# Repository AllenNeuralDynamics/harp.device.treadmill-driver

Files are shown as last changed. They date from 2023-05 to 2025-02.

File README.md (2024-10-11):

A Harp Device for controlling an instrumented variable-friction mouse treadmill

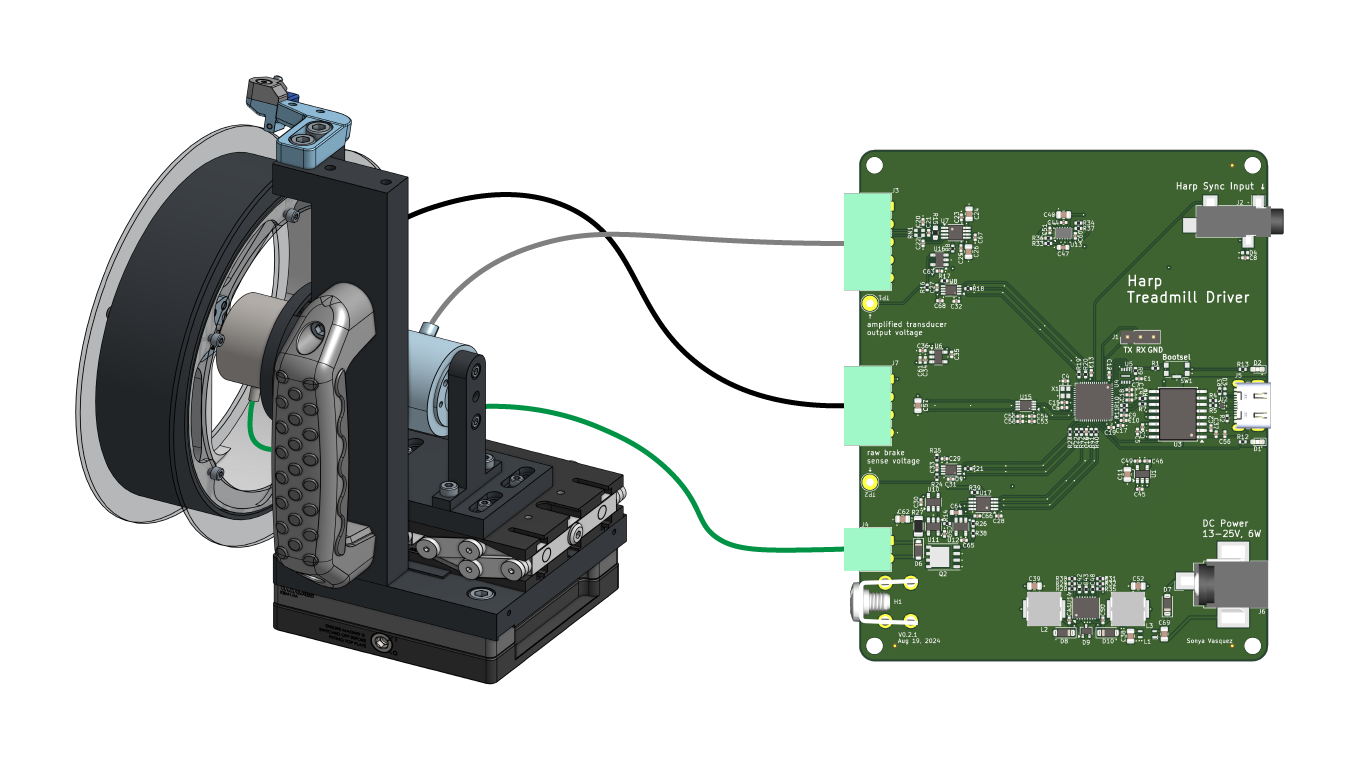
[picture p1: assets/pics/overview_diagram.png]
overview


> [!NOTE]
> This repository contains design files for the electronics assembly. For the mechanical assembly, design files, and bill-of-materials, see the [OnShape project](https://cad.onshape.com/documents/579ff6de692121d8b6a45604/v/23e1e086e9eb645d096dac80/e/a0ad881c32324c0acf8e15df).

## Features
* linear (no switching!) current control of 12V magnetic brake, Placid Industries B5ZD, [datasheet](https://placidindustries.com/d/?h=a03be4b).
* reads measurements from an [RTS-10 torque transducer](https://www.transducertechniques.com/rts-torque-sensor.aspx#)
* wheatstone bridge input for torque transducer
* quadrature encoder input for position/speed measurements
* Harp-protocol compliant over full-speed USB
* accepts Harp time synchronization input.
* reverse-polarity protected power supply.

## Register Map
[List of Registers](./firmware/docs/register_map.csv)

## Credits
This board design was created in partnership with the team at [Second Order Effects](https://soeffects.com/).

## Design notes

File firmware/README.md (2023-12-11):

## Setting up the Build Environment

### Install Submodules
This project uses the [Harp Core RP2040](https://github.com/AllenNeuralDynamics/harp.core.rp2040) library as a submodule.
Install it with:
````
git submodule update --init
````

### Install Pico SDK
This project uses the [Pico SDK](https://github.com/raspberrypi/pico-sdk/tree/master).
The SDK needs to be downloaded and installed to a known folder on your PC.
Note that the PICO SDK also contains submodules (including TinyUSB), so you must ensure that they are also fetched with:
````
git clone git clone git@github.com:raspberrypi/pico-sdk.git
git submodule update --init --recursive
````

### Point to Pico SDK
Recommended, but optional: define the `PICO_SDK_PATH` environment variable to point to the location where the pico-sdk was downloaded. i.e:
````
PICO_SDK_PATH=/home/username/projects/pico-sdk
````
On Linux, it may be preferrable to put this in your `.bashrc` file.

## Compiling the Firmware

### Without an IDE
From this directory, create a directory called build, enter it, and invoke cmake with:
````
mkdir build
cd build
cmake ..
````
If you did not define the `PICO_SDK_PATH` as an environment variable, you must pass it in here like so:
````
mkdir build
cd build
cmake -DPICO_SDK_PATH=/path/to/pico-sdk ..
````
After this point, you can invoke the auto-generated Makefile with `make`

## Flashing the Firmware
Press-and-hold the Pico's BOOTSEL button and power it up (i.e: plug it into usb).
At this point you do one of the following:
* drag-and-drop the created **\*.uf2** file into the mass storage device that appears on your pc.
* flash with [picotool](https://github.com/raspberrypi/picotool)

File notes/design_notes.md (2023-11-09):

## RP2040

### Oscillator
The RP2040 accepts either a crystal or CMOS-level clock input
I opted for a precision oscillator instead of a vanilla crystal.
To preserve USB Boot functionality (useful!), I kept the frequency at 12MHz (datasheet pg 12).

This oscillator requires a 0.01-0.1uF bypass capacitor placed very close to the pins.
An example layout is provided in the datasheet.

## USB Isolator
To disconnect the host PC's ground from this device's ground, I added a Full-Speed capable USB isolator.

The downside is that this device cannot be powered via USB from the host pc.

## Analog Front-End

# PCB Layout

## Layers

## References
* [All About USBC: Example Circuits](https://hackaday.com/2023/08/07/all-about-usb-c-example-circuits/)
  * contains schematic for a device to display itself as a full speed USB device.
* [Raspberry Pi Pico Datasheet](https://datasheets.raspberrypi.com/pico/pico-datasheet.pdf)
  * contains schematic for minimal board design.
* [AD9833 Signal Generator First Steps Part 1](https://daumemo.com/diy-ad9833-signal-generator-first-steps-part-1/)
  * Contains effect of load resistance on output voltage.
* [Hardware Design with the RP2040](https://datasheets.raspberrypi.com/rp2040/hardware-design-with-rp2040.pdf)
* [SPI: High Speed Design](https://practicalee.com/spi/)
  * source termination resistor placement.
* [Reduced Printed Circuit Board Emissions with Low-Noise Design Practices](https://ntrs.nasa.gov/api/citations/20120009353/downloads/20120009353.pdf)
* [Stack Exchange: How to Connect USB Connector Shield](https://electronics.stackexchange.com/questions/4515/how-to-connect-usb-connector-shield)
* [Driving Inductive Loads with Power Switches](https://www.ti.com/video/6018730150001#transcript-tab)
* [B5ZD Magnetic Particle Brake datasheet](https://placidindustries.com/d/?h=a03be4b)
  * this design is intended for the 12V variant.
* [Signal Chain Basics 78: How to avoid common mode limitations on instrumentation amplifiers](https://www.planetanalog.com/signal-chain-basics-78-how-to-avoid-common-mode-limitations-on-instrumentation-amplifiers/)
* [Hammond Manufacturing 1455L801 Case Drawing](https://www.hammfg.com/files/parts/pdf/1455L801.pdf)

### Reference Designs
* [LTC2641 Datasheet](https://www.analog.com/media/en/technical-documentation/data-sheets/26412fd.pdf)
  * features a programmable constant current sink in the "Typical Application" section.

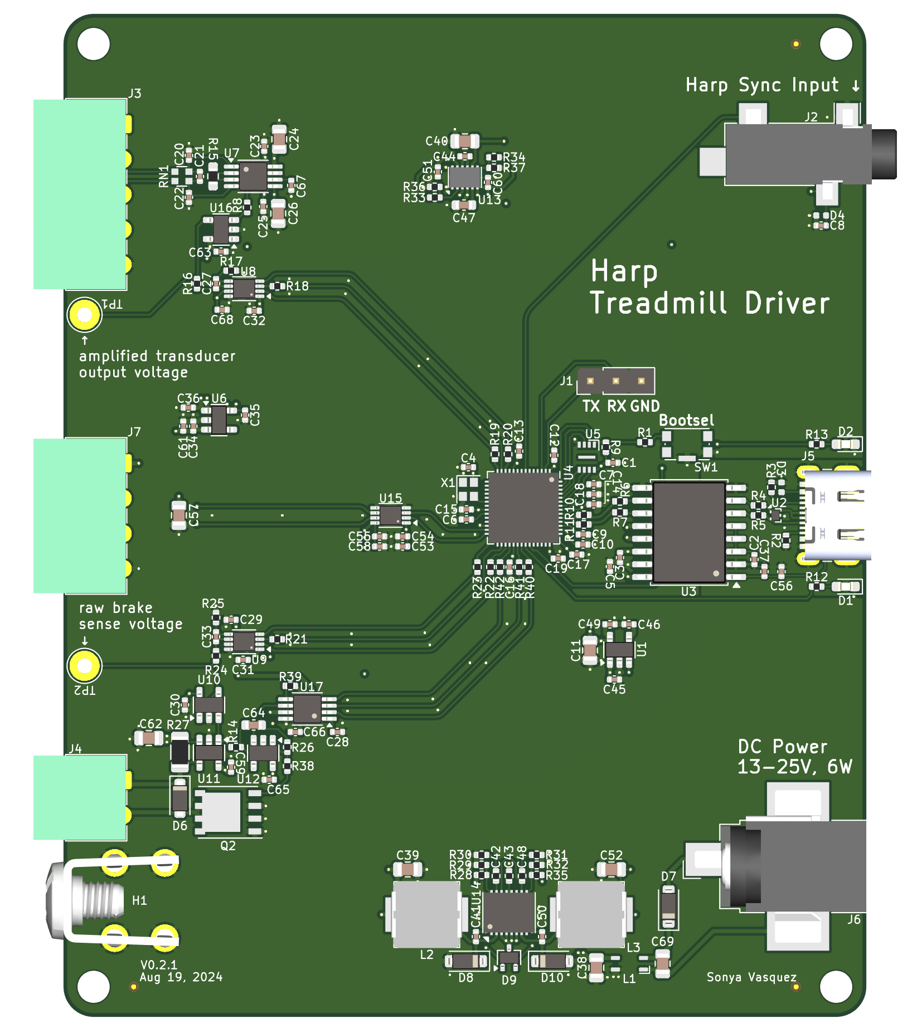
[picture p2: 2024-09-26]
assets/pics/treadmill_no_background.png

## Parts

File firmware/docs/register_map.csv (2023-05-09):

Register | Size | Read-Only | Name | Description
0x32 | U16 |  | TORQUE_SENSOR_RAW | raw measurement of the treadmill angular torque sensor.
0x33 | U16 |  | TORQUE_LOAD_CURRENT_RAW | raw measurement of the output current applied to the variable torque load.
0x34 | U32 |  | ENCODER_MEAS_RAW | raw measurement of the treadmill encoder (800 ticks per revolution).
0x35 | U32 |  | TORQUE_LOAD_SETPOINT_RAW | raw setpoint for the torque load.
0x36 | U8 |  | SUBSYSTEM_RESET | "Writing 1 to specific bits in this register will reset [0] the encoder count | [1] the torque load PI loop."

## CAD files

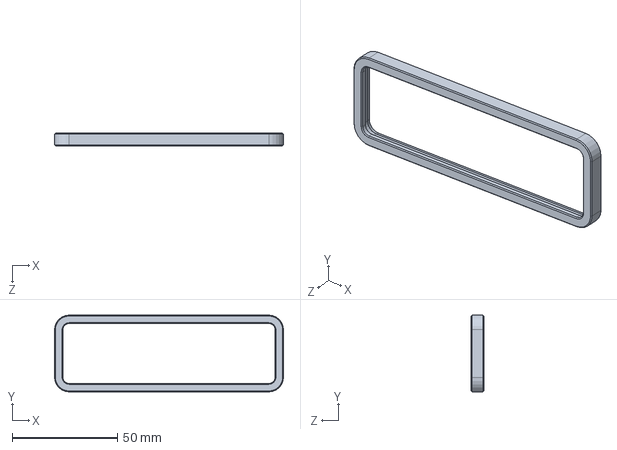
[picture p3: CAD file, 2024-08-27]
hardware/enclosure/cads/solidworks/1455L801_lids_and_trim.SLDPRT
108.9 x 36.5 x 6.00 mm

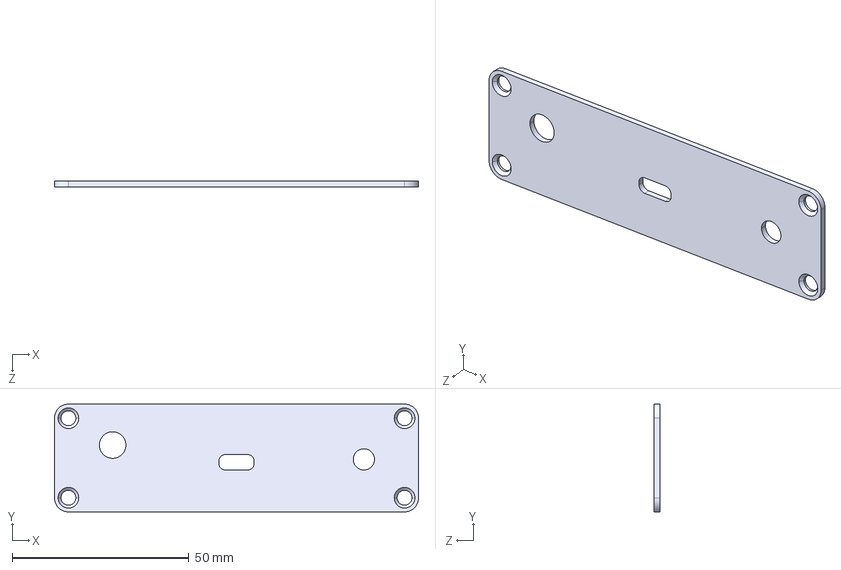
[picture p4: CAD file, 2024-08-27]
hardware/enclosure/cads/step/1455L801_lid_data_side.STEP
102.9 x 30.5 x 1.57 mm

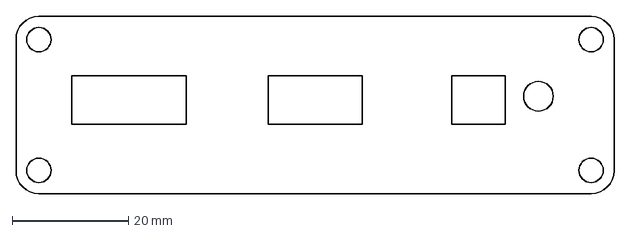
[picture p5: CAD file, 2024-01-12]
hardware/enclosure/exports/dxfs/1455L801_lid_io_side.DXF
102.9 x 30.5 mm

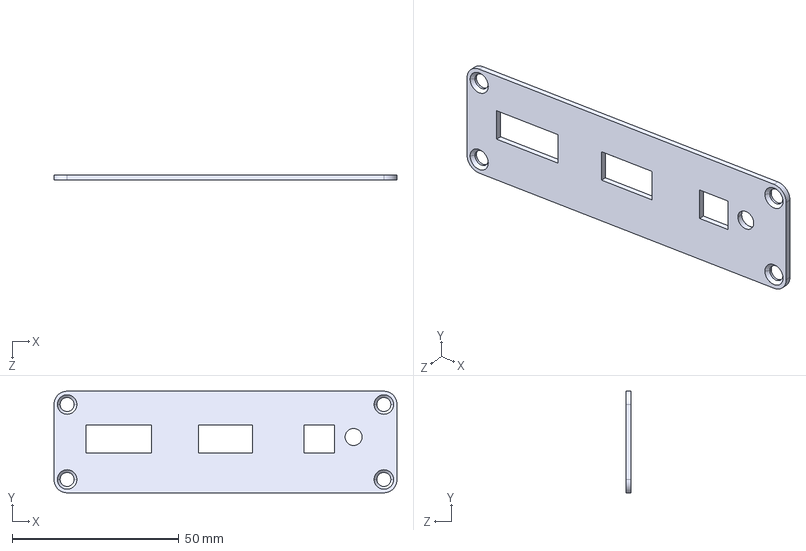
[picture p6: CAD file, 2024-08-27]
hardware/enclosure/cads/step/1455L801_lid_io_side.STEP
102.9 x 30.5 x 1.57 mm

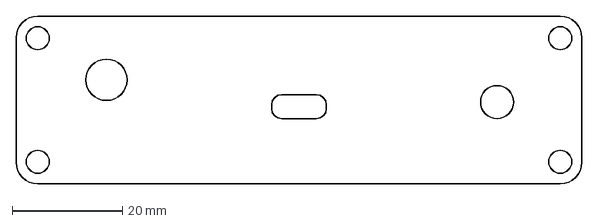
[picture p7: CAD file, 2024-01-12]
hardware/enclosure/exports/dxfs/1455L801_lid_data_side.DXF
102.9 x 30.5 mm

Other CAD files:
hardware/enclosure/exports/stls/1455L801_trim.STL

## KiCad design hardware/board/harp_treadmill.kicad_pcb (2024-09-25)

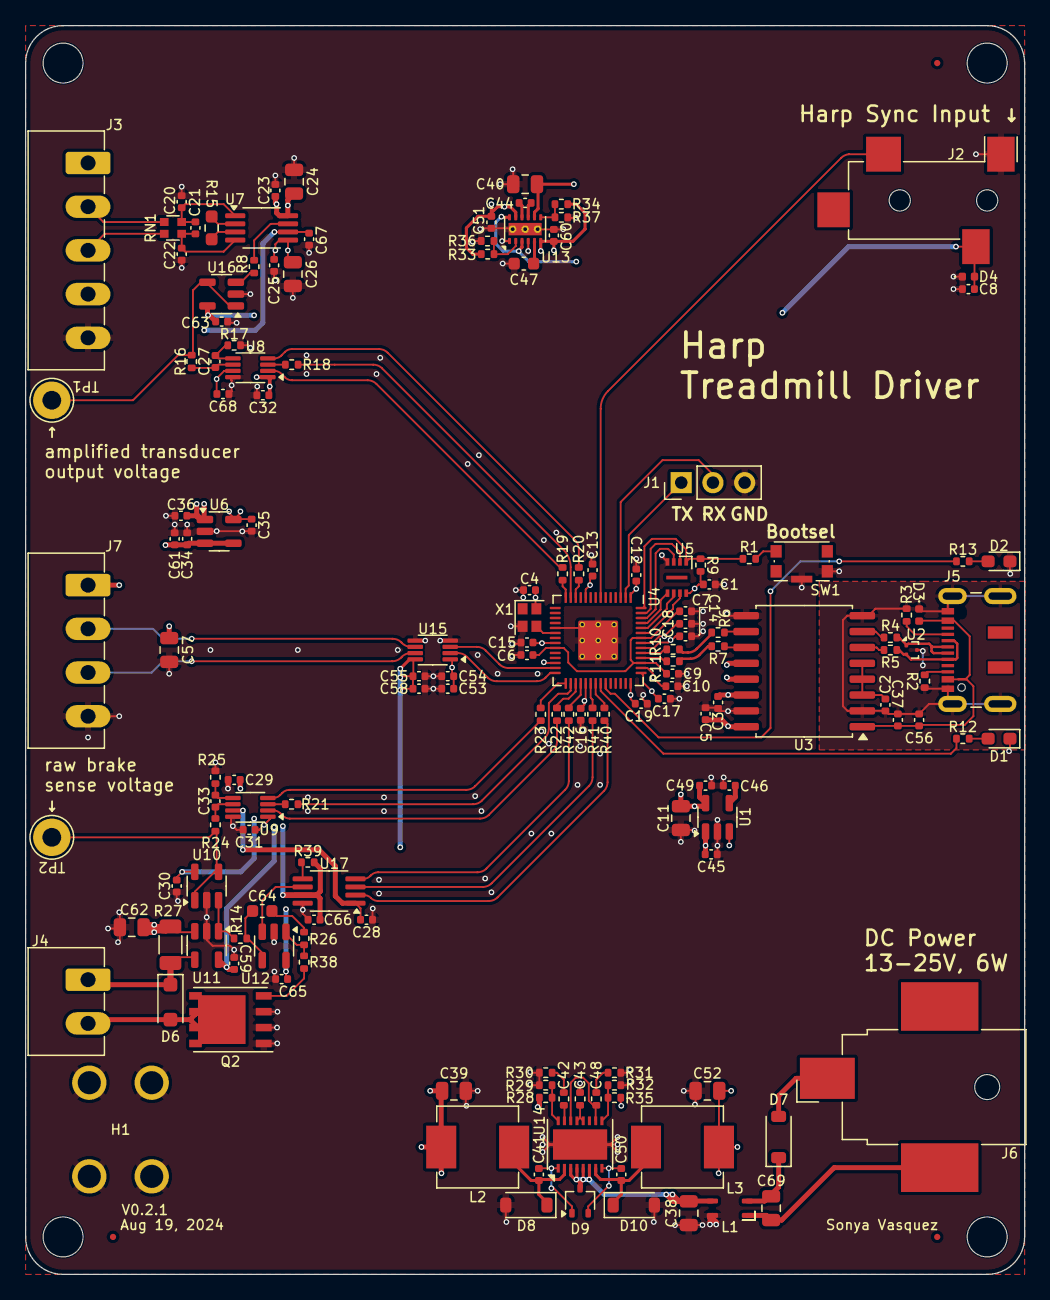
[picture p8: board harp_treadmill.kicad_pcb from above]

Board: 4 copper layers, 80.0 x 100.0 mm, 157 parts (0 on the bottom side), 105 nets.

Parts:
C1, C2, C3, C5, C6, C7, C12, C13, C14, C15, C16, C17, C18, C19, C23, C25, C28, C29, C30, C31, C32, C34, C35, C36, C37, C41, C50, C53, C58, C59, C63, C65, C66, C67, C68: 100nF; C_0402_1005Metric
C4, C46: 10nF; C_0402_1005Metric
C8, C9, C10, C44, C45, C54, C55, C56, C61: 1uF; C_0402_1005Metric
C11, C24, C26, C38, C57, C62, C69: 10uF; C_0805_2012Metric
C20, C22: 100pF; C_0402_1005Metric
C21: 1000pF; C_0402_1005Metric
C27, C33: 300pF; C_0402_1005Metric
C39, C40, C52: 22uF; C_0805_2012Metric
C42, C48: 1.5nF; R_0402_1005Metric
C43: 4.7nF; R_0402_1005Metric
C47: 4.7uF; C_0603_1608Metric
C49, C51, C60: 2.2uF; C_0402_1005Metric
C64: 10nF; C_0603_1608Metric
D1, D2: LED; LED_0603_1608Metric_Pad1.05x0.95mm_HandSolder
D3, D4: D_TVS; D_0402_1005Metric
D6: 1N4007FL; D_SOD-123F
D7, D8, D10: D_Schottky; D_SOD-123
D9: BAT54AW; SOT-323_SC-70
FID1, FID2, FID3: Fiducial; Fiducial_0.5mm_Mask1mm
H1: MountingHole_Pad; Terminal_Keystone_779x_EdgeMount_Horizontal
J1: Conn_01x03_Male; PinHeader_1x03_P2.54mm_Vertical
J2: AudioJack3; Jack_3.5mm_CUI_SJ-3524-SMT_Horizontal
J3: Conn_01x05_Female; PhoenixContact_MC_1,5_5-G-3.5_1x05_P3.50mm_Horizontal
J4: Conn_01x02_Female; PhoenixContact_MC_1,5_2-G-3.5_1x02_P3.50mm_Horizontal
J5: USB_C_Receptacle_USB2.0; USB_C_Receptacle_JAE_DX07S016JA1R1500
J6: Barrel_Jack_Switch; BarrelJack_CUI_PJ-036AH-SMT_Horizontal
J7: Conn_01x04_Female; PhoenixContact_MC_1,5_4-G-3.5_1x04_P3.50mm_Horizontal
L1: L_Coupled_1423; L_CommonModeChoke_TDKCorporation_1210
L2, L3: 10uH; L_Vishay_IHLP-2525
Q2: Si7336ADP; PowerPAK_SO-8_Single
R1: 1K; R_0402_1005Metric
R2, R3, R26: 5K1; R_0402_1005Metric
R4, R5, R6, R7: 24; R_0402_1005Metric
R8, R9, R28, R30, R31, R35, R39: 10K; R_0402_1005Metric
R10, R11: 27; R_0402_1005Metric
R12, R13: 680; R_0402_1005Metric
R14: 7K5; R_0402_1005Metric
R15: 499; R_0603_1608Metric_Pad0.98x0.95mm_HandSolder
R16, R17, R24, R25: 100; R_0402_1005Metric
R18, R19, R20, R21, R22, R23, R40, R41, R42: 49.9; R_0402_1005Metric
R27: 0.08; R_1206_3216Metric
R29: 715; R_0402_1005Metric
R32: 1K82; R_0402_1005Metric
R33: 162K; R_0402_1005Metric
R34: 158K; R_0402_1005Metric
R36, R37: 51K; R_0402_1005Metric
R38: 10; R_0402_1005Metric
RN1: 20K; R_Array_Convex_2x0606
SW1: SW_Push_1P1T-SH_NO_Vertical_Wuerth_WS-TASV
TP1, TP2: TestPoint; TestPoint_THTPad_D3.0mm_Drill1.5mm
U1: LP2985-3.3; SOT-23-5
U2: TPD2EUSB30; Texas_DRT-3
U3: ADUM4160; SOIC-16W_7.5x10.3mm_P1.27mm
U4: RP2040; RP2040-QFN-56
U5: W25Q16JVUXIQ; Winbond-8USON-2x3mm
U6: REF2033; SOT-23-5
U7: AD8226; MSOP-8_3x3mm_P0.65mm
U8, U9: ADS7049; VSSOP-8_2.3x2mm_P0.5mm
U10, U12, U16: AD8615; TSOT-23-5
U11: INA180A4; SOT-23-5
U13: LM27762; WSON-12-1EP_3x2mm_P0.5mm_EP1x2.65_ThermalVias
U14: LT3506; DFN-16-1EP_4x5mm_P0.5mm_EP2.44x4.34mm
U15: 74LVCH2T45DC; VSSOP-8_2.3x2mm_P0.5mm
U17: LTC2641; MSOP-8_3x3mm_P0.65mm
X1: ECS-TXO-2016; Crystal_SMD_2016-4Pin_2.0x1.6mm

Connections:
5V2: C34.2, C40.1, C45.1, C52.1, C55.1, C57.1, C58.2, C61.1, C65.2, J7.1, L3.2, R35.1, U1.1 (VIN), U1.3 (ON/~OFF), U6.3 (EN), U6.4 (VIN), U12.5 (V+), U13.3 (VIN), U13.8 (EN-), U13.12 (EN+), U15.8 (VCCB)
+1V1: C6.2, C7.2, C9.1, U4.23 (DVDD), U4.45 (VREG_VOUT), U4.50 (DVDD)
+3V3: C1.2, C3.2, C4.2, C5.2, C8.1, C10.1, C11.1, C12.2, C13.2, C14.2, C15.2, C16.2, C17.2, C18.2, C19.2, C30.2, C31.2, C32.2, C49.2, C53.2, C54.1, C59.2, C63.2, C66.2, D4.2 (A2), J2.R, R9.2, R39.2, U1.5 (VOUT), U3.12 (PIN), U3.13 (SPD), U3.14 (VDD2), U3.16 (VBUS2), U4.1 (IOVDD), U4.10 (IOVDD), U4.22 (IOVDD), U4.26 (RUN), U4.33 (IOVDD), U4.42 (IOVDD), U4.43 (ADC_AVDD), U4.44 (VREG_IN), U4.48 (USB_VDD), U4.49 (IOVDD), U5.8 (VCC), U8.1 (DVDD), U9.1 (DVDD), U10.5 (V+), U11.5 (V+), U15.1 (VCCA), U16.5 (V+), U17.7 (VDD), X1.4 (VDD)
+5V: C23.2, C24.1, C51.2, J3.1, R33.1, U7.8 (V+), U13.11 (OUT+)
+12V: C39.1, C62.1, L2.1, R27.1, R28.2, U11.3 (+)
-5V: C25.2, C26.2, C60.2, J3.4, R34.1, U7.5 (V-), U13.6 (OUT-)
/Encoder/ENC_A: U4.27 (GPIO16), U15.3 (2A)
/Encoder/ENC_B: U4.28 (GPIO17), U15.2 (1A)
/Harp Core RP2040 + Isolated USB/D+: J5.A6 (D+), J5.B6 (D+), R4.1, U2.1 (D+)
/Harp Core RP2040 + Isolated USB/D-: J5.A7 (D-), J5.B7 (D-), R5.1, U2.2 (D-)
/Harp Core RP2040 + Isolated USB/DD+: R6.2, R10.2
/Harp Core RP2040 + Isolated USB/DD-: R7.2, R11.2
/Harp Core RP2040 + Isolated USB/HARP_CLK_SYNC: J2.T, U4.7 (GPIO5)
/Harp Core RP2040 + Isolated USB/PIO_ADC0_CS: R23.2, U4.29 (GPIO18)
/Harp Core RP2040 + Isolated USB/PIO_ADC0_POCI: R21.2, U4.30 (GPIO19)
/Harp Core RP2040 + Isolated USB/PIO_ADC0_SCK: R22.2, U4.31 (GPIO20)
/Harp Core RP2040 + Isolated USB/PIO_ADC1_CS: R20.2, U4.12 (GPIO9)
/Harp Core RP2040 + Isolated USB/PIO_ADC1_POCI: R18.2, U4.13 (GPIO10)
/Harp Core RP2040 + Isolated USB/PIO_ADC1_SCK: R19.2, U4.14 (GPIO11)
/Harp Core RP2040 + Isolated USB/PIO_DAC_CS: R40.2, U4.35 (GPIO23)
/Harp Core RP2040 + Isolated USB/PIO_DAC_PICO: R42.2, U4.32 (GPIO21)
/Harp Core RP2040 + Isolated USB/PIO_DAC_SCK: R41.2, U4.34 (GPIO22)
/Harp Core RP2040 + Isolated USB/QSPI_CLK: U4.52 (QSPI_SCLK), U5.6 (CLK)
/Harp Core RP2040 + Isolated USB/QSPI_CS: R1.2, R9.1, U4.56 (QSPI_SS), U5.1 (~CS)
/Harp Core RP2040 + Isolated USB/QSPI_D0: U4.53 (QSPI_SD0), U5.5 (DI(IO0))
/Harp Core RP2040 + Isolated USB/QSPI_D1: U4.55 (QSPI_SD1), U5.2 (DO(IO1))
/Harp Core RP2040 + Isolated USB/QSPI_D2: U4.54 (QSPI_SD2), U5.3 (IO2)
/Harp Core RP2040 + Isolated USB/QSPI_D3: U4.51 (QSPI_SD3), U5.7 (IO3)
/Harp Core RP2040 + Isolated USB/UART0_RXD: J1.2, U4.3 (GPIO1)
/Harp Core RP2040 + Isolated USB/UART0_TXD: J1.1, U4.2 (GPIO0)
/Harp Core RP2040 + Isolated USB/USB_Boot: R1.1, SW1.2
/Harp Core RP2040 + Isolated USB/VDD1: C2.2, U3.3 (VDD1), U3.4 (PDEN), U3.5 (SPU)
GND: C1.1, C3.1, C4.1, C5.1, C6.1, C7.1, C8.2, C9.2, C10.2, C11.2, C12.1, C13.1, C14.1, C15.1, C16.1, C17.1, C18.1, C19.1, C20.1, C22.2, C23.1, C24.2, C25.1, C26.1, C28.1, C29.1, C30.1, C31.1, C32.1, C34.1, C35.1, C36.1, C38.2, C39.2, C40.2, C43.1, C45.2, C46.2, C47.2, C49.1, C51.1, C52.2, C53.1, C54.2, C55.2, C57.2, C58.1, C59.1, C60.1, C61.2, C62.2, C63.1, C65.1, C66.1, C67.1, C68.1, D1.1 (K), D2.1 (K), D4.1 (A1), D8.2 (A), D10.2 (A), H1.1, J1.3, J2.S, J3.5, J7.4, L1.4, Q2.1 (S), Q2.2 (S), Q2.3 (S), R17.1, R25.1, R29.2, R30.1, R31.1, R32.1, R36.2, R37.2, SW1.4, SW1.SH, U1.2 (GND), U3.9 (GND2), U3.15 (GND2), U4.19 (TESTEN), U4.57 (GND), U5.4 (GND), U6.2 (GND), U8.8 (GND), U9.8 (GND), U10.2 (V-), U11.2 (GND), U12.2 (V-), U13.1 (PGOOD), U13.4 (GND), U13.13 (PAD), U14.17 (GND), U15.4 (GND), U15.5 (DIR), U16.2 (V-), U17.8 (GND), X1.2 (GND)
GND1: C2.1, C37.1, C56.2, D3.1 (A1), J5.A1 (GND), J5.A12 (GND), J5.B1 (GND), J5.B12 (GND), J5.S1 (SHIELD), R2.2, R3.2, U2.3 (GND), U3.2 (GND1), U3.8 (GND1)
GND2: C69.2, J6.2, L1.1
unnamed: C42.1, R30.2
unnamed: C48.2, R31.2
unnamed: C64.2, R26.1
unnamed: D1.2 (A), R12.2
unnamed: D2.2 (A), R13.2
unnamed: D6.2 (A), J4.2, Q2.5 (D)
unnamed: D6.1 (K), J4.1, R27.2, U11.4 (-)
unnamed: C69.1, D7.1 (K), L1.2
unnamed: C41.1, D8.1 (K), L2.2, U14.2 (SW1)
unnamed: C50.1, D10.1 (K), L3.1, U14.7 (SW2)
unnamed: J3.2, RN1.1 (R1.1)
unnamed: J3.3, RN1.2 (R2.1)
unnamed: J5.A5 (CC1), R2.1
unnamed: J5.B5 (CC2), R3.1
unnamed: J7.2, U15.6 (2B)
unnamed: J7.3, U15.7 (1B)
unnamed: Q2.4 (G), R38.2
unnamed: R15.1, U7.2 (RG)
unnamed: R15.2, U7.3 (RG)
unnamed: R26.2, R38.1, U12.1
unnamed: C20.2, C21.1, RN1.4 (R1.2), U7.1 (IN-)
unnamed: C21.2, C22.1, RN1.3 (R2.2), U7.4 (IN+)
unnamed: C46.1, U1.4 (BP)
unnamed: R6.1, U3.10 (DD+)
unnamed: R7.1, U3.11 (DD-)
unnamed: R4.2, U3.7 (UD+)
unnamed: R5.2, U3.6 (UD-)
unnamed: R12.1, U4.36 (GPIO24)
unnamed: R13.1, U4.37 (GPIO25)
unnamed: R11.1, U4.46 (USB_DM)
unnamed: R10.1, U4.47 (USB_DP)
unnamed: U4.20 (XIN), X1.3 (OUT)
unnamed: R8.2, U7.7 (VOUT)
unnamed: C27.2, R17.2, U8.5 (AINM)
unnamed: C27.1, R16.1, U8.6 (AINP)
unnamed: R19.1, U8.2 (SCLK)
unnamed: R18.1, U8.3 (SDO)
unnamed: R20.1, U8.4 (~CS)
unnamed: C33.2, R25.2, U9.5 (AINM)
unnamed: C33.1, R24.1, U9.6 (AINP)
unnamed: R22.1, U9.2 (SCLK)
unnamed: R21.1, U9.3 (SDO)
unnamed: R23.1, U9.4 (~CS)
unnamed: R14.1, U10.3 (+), U11.1
unnamed: R24.2, TP2.1, U10.1, U10.4 (-)
unnamed: U12.3 (+), U17.6 (VOUT)
unnamed: C64.1, R14.2, U12.4 (-)
unnamed: C44.1, U13.10 (C+)
unnamed: C44.2, U13.9 (C-)
unnamed: C47.1, U13.5 (CP)
unnamed: R33.2, R36.1, U13.2 (FB+)
unnamed: R34.2, R37.1, U13.7 (FB-)
unnamed: C41.2, D9.1, U14.1 (BOOST1)
unnamed: C50.2, D9.2, U14.8 (BOOST2)
unnamed: R28.1, R29.1, U14.16 (FB1)
unnamed: R32.2, R35.2, U14.9 (FB2)
unnamed: C48.1, U14.10 (VC2), U14.14 (PG1)
unnamed: C43.2, U14.12 (RUN/SS2), U14.13 (RUN/SS1)
unnamed: C42.2, U14.15 (VC1)
unnamed: R8.1, U16.3 (+)
unnamed: R16.2, TP1.1, U16.1, U16.4 (-)
unnamed: R42.1, U17.4 (DIN)
unnamed: R41.1, U17.3 (SCLK)
unnamed: R39.1, U17.5 (~CLR)
unnamed: R40.1, U17.2 (~CS)
VBUS: C37.2, C56.1, D3.2 (A2), J5.A4 (VBUS), J5.A9 (VBUS), J5.B4 (VBUS), J5.B9 (VBUS), U3.1 (VBUS1)
VIN1: C38.1, D9.3, L1.3, U14.3 (VIN1), U14.4 (VIN1), U14.5 (VIN2), U14.6 (VIN2)
VPP: D7.2 (A), J6.1
VREF_1V65: C36.2, C67.2, U6.1 (VBIAS), U7.6 (REF)
VREF_3V3: C28.2, C29.2, C35.2, C68.2, U6.5 (VREF), U8.7 (AVDD), U9.7 (AVDD), U17.1 (REF)

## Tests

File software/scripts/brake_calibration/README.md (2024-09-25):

# Magnetic Brake Calibration

## Hardware Setup
* *Jrk G2 21v3 USB Motor Controller* connected to the PC and powered on.

## Installation

Download the [Jrk G2 Software](https://www.pololu.com/product/3142/resources) for your target system and install it.

Install the script dependencies with:
````bash
pip install -r requirements.txt
````

## References
* [jrk2cmd Command Reference](https://www.pololu.com/docs/0J73/11)
* [jrk2cmd Python example](https://www.pololu.com/docs/0J73/15.3)

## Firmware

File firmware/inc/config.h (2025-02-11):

#ifndef CONFIG_H
#define CONFIG_H

#define HW_VERSION_MAJOR (0)
#define HW_VERSION_MINOR (2)
#define HW_VERSION_PATCH (1)

#define FW_VERSION_MAJOR (0)
#define FW_VERSION_MINOR (1)
#define FW_VERSION_PATCH (3)

#define UART_TX_PIN (0) // for printf-style debugging.
#define HARP_SYNC_RX_PIN (5)
#define LED0 (24)
#define LED1 (25)

#define ENCODER_BASE_PIN (16) // 16 = A, 17 = B

// Brake Current ADC
#define BRAKE_CURRENT_CS_PIN (18)
#define BRAKE_CURRENT_POCI_PIN (19)
#define BRAKE_CURRENT_SCK_PIN (20)

// Torque Transducer ADC
#define TORQUE_TRANSDUCER_CS_PIN (9)
#define TORQUE_TRANSDUCER_POCI_PIN (10)
#define TORQUE_TRANSDUCER_SCK_PIN (11)

// Torque Transducer safety limits.
// Note: not all transducers can physcially reach 0 and 4095 extremes.
#define RAW_TORQUE_SENSOR_MIN (100)
#define RAW_TORQUE_SENSOR_MAX (3995) // 12-bit.

// Brake Setpoint DAC
#define BRAKE_SETPOINT_CS_PIN (23)
#define BRAKE_SETPOINT_PICO_PIN (21)
#define BRAKE_SETPOINT_SCK_PIN (22)

#define MAX_EVENT_FREQUENCY_HZ (1000)


#define TREADMILL_HARP_DEVICE_ID (0x057A)

#endif // CONFIG_H

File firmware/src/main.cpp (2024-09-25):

#include <pico/stdlib.h>
#include <cstring>
#include <pio_encoder.h>
#include <pio_ads7049.h>
#include <pio_ltc264x.h>
#include <config.h>
#include <harp_message.h>
#include <harp_core.h>
#include <harp_c_app.h>
#include <harp_synchronizer.h>
#ifdef DEBUG
    #include <cstdio> // for printf
#endif

// encoder program is 29 instructions, so it needs to go on its own PIO slice.
PIOEncoder encoder(pio1, 0, ENCODER_BASE_PIN);
// Create PIO SPI ADC instances for current and torque transducer sensing.
// Both PIO_ADS7049 instances can use the same PIO program.
PIO_ADS7049 current_sensor(pio0,
                           BRAKE_CURRENT_CS_PIN,
                           BRAKE_CURRENT_SCK_PIN, BRAKE_CURRENT_POCI_PIN);
// Use PIO_ADS7049 program already-loaded by current sensor.
PIO_ADS7049 reaction_torque_sensor(pio0, TORQUE_TRANSDUCER_CS_PIN,
                                   TORQUE_TRANSDUCER_SCK_PIN,
                                   TORQUE_TRANSDUCER_POCI_PIN,
                                   current_sensor.get_program_address());
// Create PIO SPI DAC instance for driving the brake current setpoint.
PIO_LTC264x brake_setpoint(pio0, // CS pin is SCK pin + 1
                           BRAKE_SETPOINT_SCK_PIN,
                           BRAKE_SETPOINT_PICO_PIN);



// Create device name array.
const uint16_t who_am_i = TREADMILL_HARP_DEVICE_ID;
const uint8_t assembly_version = 0;
const uint8_t harp_version_major = 0;
const uint8_t harp_version_minor = 0;
const uint16_t serial_number = 0;

// Setup for Harp App
const size_t reg_count = 10;

uint32_t __not_in_flash("dispatch_interval_us") dispatch_interval_us;
uint32_t __not_in_flash("next_msg_dispatch_time_us") next_msg_dispatch_time_us;

// PIO and DMA will periodically write raw values to these locations.
volatile uint32_t __not_in_flash("encoder_raw") encoder_raw;
volatile int16_t __not_in_flash("torque_raw") torque_raw;
volatile int16_t __not_in_flash("brake_current_raw") brake_current_raw;

// Filtered value for torque limit.
volatile int32_t __not_in_flash("filtered_torque") filtered_torque;
uint32_t __not_in_flash("torque_limit_interval_us") torque_limit_interval_us;
uint32_t __not_in_flash("next_torque_check_time_us") next_torque_check_time_us;

// offset --> measurement taken at requested time.
int32_t __not_in_flash("encoder_offset") encoder_offset;
int16_t __not_in_flash("torque_offset") torque_offset;
int16_t __not_in_flash("brake_current_offset") brake_current_offset;

inline uint32_t get_tared_encoder_ticks()
{ return encoder_raw - encoder_offset;}

// DMA writes the data to torque_raw and brake_current_raw word-by-word
// (2 bytes at a time in this case).
// Subtlety: these "getter functions" make an atomic copy of the data at the
// location that DMA is writing to into the CPU registers before doing the
// subtraction, hence preventing part of the word (1 of 2 bytes) from being
// overwritten by DMA while this function executes.
inline int16_t get_tared_reaction_torque()
{ return torque_raw - torque_offset;}
inline int16_t get_tared_brake_current()
{ return brake_current_raw - brake_current_offset;}

#pragma pack(push, 1)
struct app_regs_t
{
    int32_t encoder_ticks;   // 32.
    int16_t reaction_torque;  // 33. 12-bit. underlying measurement is signed.
    int16_t brake_current;    // 34. 12-bit. underlying measurement is unsigned
                              //   but can go negative because of tare value.
    int32_t sensors[3]; // aggregate vector of the above 3 three registers:
                         // [position, uint32(torque), uint32(current)]
    uint16_t sensor_dispatch_frequency_hz;  // 36
    uint16_t brake_current_setpoint;    // 37. 16-bit full-scale range,
                                        // but 12-bit resolution. Unsigned.
                                        // This value is cleared to 0 if
                                        // torque_limiting is enabled and
                                        // triggered. Further writes in this
                                        // condition return a WRITE_ERROR.
    uint8_t tare;       // {unused[7:3], brake_current[2], torque[1], encoder[0]}
    uint8_t reset_tare; // {unused[7:3], brake_current[2], torque[1], encoder[0]}
    uint8_t torque_limiting;    // 1 --> Disable of the brake if the
                                //       maximum torque sensor value is detected.
                                //       This feature prevents the reaction
                                //       torque sensor from being damaged.
                                //       Resets to this state.
                                // 0 --> Do not disable the brake if the
                                //       maximum torque sensor is detected.
    uint8_t torque_limiting_triggered; // 1 --> torque limit triggered. Brake
                                       //       is disabled and
                                       //       brake_current_setpoint is
                                       //       set to 0.
                                       //       An EVENT msg is sent when this
                                       //       value occurs.
                                       // Write 0 to clear the torque-limit
                                       // condition and re-enable the brake.
    // More app "registers" here.
};
#pragma pack(pop)
app_regs_t __not_in_flash("app_regs") app_regs;

// Define "specs" per-register
RegSpecs app_reg_specs[reg_count]
{
    {(uint8_t*)&app_regs.encoder_ticks, sizeof(app_regs.encoder_ticks), S32},
    {(uint8_t*)&app_regs.reaction_torque, sizeof(app_regs.reaction_torque), S16},
    {(uint8_t*)&app_regs.brake_current, sizeof(app_regs.brake_current), S16},
    {(uint8_t*)&app_regs.sensors, sizeof(app_regs.sensors), S32},
    {(uint8_t*)&app_regs.sensor_dispatch_frequency_hz, sizeof(app_regs.sensor_dispatch_frequency_hz), U16},
    {(uint8_t*)&app_regs.brake_current_setpoint, sizeof(app_regs.brake_current_setpoint), U16},
    {(uint8_t*)&app_regs.tare, sizeof(app_regs.tare), U8},
    {(uint8_t*)&app_regs.reset_tare, sizeof(app_regs.reset_tare), U8},
    {(uint8_t*)&app_regs.torque_limiting, sizeof(app_regs.torque_limiting), U8},
    {(uint8_t*)&app_regs.torque_limiting_triggered, sizeof(app_regs.torque_limiting_triggered), U8}
    // More specs here if we add additional registers.
};

void write_sensor_dispatch_frequency_hz(msg_t& msg)
{
    msg_type_t msg_reply_type = WRITE;
    HarpCore::copy_msg_payload_to_register(msg);
    // Clamp maximum value.
    if (app_regs.sensor_dispatch_frequency_hz > MAX_EVENT_FREQUENCY_HZ)
    {
        // Update register and dependedent values.
        app_regs.sensor_dispatch_frequency_hz = MAX_EVENT_FREQUENCY_HZ;
        msg_reply_type = WRITE_ERROR;
    }
    if (app_regs.sensor_dispatch_frequency_hz > 0)
    {
        dispatch_interval_us = div_u32u32(1'000'000,
                                          uint32_t(app_regs.sensor_dispatch_frequency_hz));
    }
    // Update next time to dispatch.
    next_msg_dispatch_time_us = time_us_32();
    HarpCore::send_harp_reply(msg_reply_type, msg.header.address);
}

void write_brake_current_setpoint(msg_t& msg)
{
    // Note: LTC2641 driver clamps the resolution to 12-bit even though the
    // full-scale range is 16 bit.
    // Note: offset is not applied to desired current setpoint because it is
    //  distinct from measured current.
    if (app_regs.torque_limiting_triggered) // i.e: brake should be disabled.
    {
        HarpCore::send_harp_reply(WRITE_ERROR, msg.header.address);
        return;
    }
    HarpCore::copy_msg_payload_to_register(msg);
    brake_setpoint.write_value(app_regs.brake_current_setpoint);
    HarpCore::send_harp_reply(WRITE, msg.header.address);
}

void write_tare(msg_t& msg)
{
    HarpCore::copy_msg_payload_to_register(msg);
    // Handle bits to apply tare value.
    if (1u << 0 & app_regs.tare) // Zero encoder
        encoder_offset = encoder_raw;
    if (1u << 1 & app_regs.tare) // Zero reaction torque sensor
        torque_offset = torque_raw;
    if (1u << 2 & app_regs.tare) // Zero brake current sensor
        brake_current_offset = brake_current_raw;
    HarpCore::send_harp_reply(WRITE, msg.header.address);
}

void write_reset_tare(msg_t& msg)
{
    HarpCore::copy_msg_payload_to_register(msg);
    // Handle bits to clear tare value.
    if (1u << 0 & app_regs.tare) // Reset encoder to native value.
    {
        encoder_offset = 0;
        app_regs.tare &= ~(1u << 0); // Also clear tare setting in tare register.
    }
    if (1u << 1 & app_regs.tare) // Remove reaction torque sensor offset.
    {
        torque_offset = 0;
        app_regs.tare &= ~(1u << 1); // Also clear tare setting in tare register.
    }
    if (1u << 2 & app_regs.tare) // Remove brake current sensor offset.
    {
        brake_current_offset = 0;
        app_regs.tare &= ~(1u << 2); // Also clear tare setting in tare register.
    }
    // Clear register since it reads as 0.
    app_regs.reset_tare = 0;
    HarpCore::send_harp_reply(WRITE, msg.header.address);
}

void read_reg_encoder_ticks(uint8_t reg_name)
{
    app_regs.encoder_ticks = get_tared_encoder_ticks();
    HarpCore::send_harp_reply(READ, reg_name);
}

void read_reg_reaction_torque(uint8_t reg_name)
{
    app_regs.reaction_torque = get_tared_reaction_torque();
    HarpCore::send_harp_reply(READ, reg_name);
}

void read_reg_brake_current(uint8_t reg_name)
{
    app_regs.brake_current = get_tared_brake_current();
    HarpCore::send_harp_reply(READ, reg_name);
}

void update_sensor_register()
{
    app_regs.sensors[0] = get_tared_encoder_ticks();
    // Both torque sensor and brake current sensor are signed int16s, but
    // we promote to int32 for now to send an array of one type as a single msg.
    app_regs.sensors[1] = int32_t(get_tared_reaction_torque());
    app_regs.sensors[2] = int32_t(get_tared_brake_current());
}

void read_reg_sensors(uint8_t reg_name)
{
    update_sensor_register();
    HarpCore::send_harp_reply(READ, reg_name);
}

void update_torque_limit_monitor()
{
    // Check measured torque limit and disable the brake if we measure either
    // limit.
    // Bail early if torque limiting is unset or we already tripped it.
    if (!app_regs.torque_limiting || app_regs.torque_limiting_triggered)
        return;
    // y[n] = 15/16 * y[n-1] + 1/16 * x[n]
    filtered_torque = ((filtered_torque*15) >> 4) + (torque_raw >> 4);
    if (filtered_torque > RAW_TORQUE_SENSOR_MIN && filtered_torque < RAW_TORQUE_SENSOR_MAX)
        return;
    // Kill the brake; clear the current brake setpoint.
    app_regs.brake_current_setpoint = 0;
    brake_setpoint.write_value(0);
    app_regs.torque_limiting_triggered = 1; //i.e: brake disabled.
    if (HarpCore::is_muted())
        return;
    const uint8_t address_offset = 9; // torque_limiting_triggered reg.
    HarpCore::send_harp_reply(EVENT, (APP_REG_START_ADDRESS + address_offset));
}

RegFnPair reg_handler_fns[reg_count]
{
    {&read_reg_encoder_ticks, &HarpCore::write_to_read_only_reg_error},
    {&read_reg_reaction_torque, &HarpCore::write_to_read_only_reg_error},
    {&read_reg_brake_current, &HarpCore::write_to_read_only_reg_error},
    {&read_reg_sensors, &HarpCore::write_to_read_only_reg_error},
    {&HarpCore::read_reg_generic, &write_sensor_dispatch_frequency_hz},
    {&HarpCore::read_reg_generic, &write_brake_current_setpoint},
    {&HarpCore::read_reg_generic, &write_tare},
    {&HarpCore::read_reg_generic, &write_reset_tare},
    {&HarpCore::read_reg_generic, &HarpCore::write_reg_generic},
    {&HarpCore::read_reg_generic, &HarpCore::write_reg_generic}
    // More handler function pairs here if we add additional registers.
};
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

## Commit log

2023-04-10 add schematic draft
    [harp_treadmill.kicad_pcb, harp_treadmill.kicad_sch]
2023-04-14 draft torque load sensing in schematic
    [torque_load_driving.kicad_sch, torque_load_sensing.kicad_sch]
2023-04-15 adc reading works
    [harp_treadmill.kicad_sch, torque_load_sensing.kicad_sch]
2023-05-09 debug port works; draft current driver
    [harp_treadmill.kicad_sch, torque_load_sensing.kicad_sch]
2023-05-09 add preliminary register map.
    [register_map.csv]
2023-10-18 update board schematic
    [harp_treadmill.kicad_sch, torque_load_driving.kicad_sch, torque_load_sensing.kicad_sch]
2023-10-19 update pcb
    [encoder_5_to_3v3.kicad_sch, harp_core_rp2040_w_isolated_usb.kicad_sch, harp_treadmill.kicad_sch, power_supplies.kicad_sch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]
2023-10-20 update schematic
    [encoder_5_to_3v3.kicad_sch, harp_core_rp2040_w_isolated_usb.kicad_sch, harp_treadmill.kicad_sch, power_supplies.kicad_sch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]
2023-10-26 update sch and pcb
    [encoder_5_to_3v3.kicad_sch, harp_core_rp2040_w_isolated_usb.kicad_sch, harp_treadmill.kicad_pcb, harp_treadmill.kicad_sch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]
2023-10-27 update schematic; continue pcb draft
    [encoder_5_to_3v3.kicad_sch, harp_core_rp2040_w_isolated_usb.kicad_sch, harp_treadmill.kicad_pcb, harp_treadmill.kicad_sch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]
2023-10-27 wrap up pcb draft
    [harp_treadmill.kicad_pcb]
2023-10-30 update schematic annotation
    [power_supplies.kicad_sch, torque_load_sensing.kicad_sch]
2023-11-09 draft layout with analog brake driver circuit
    [encoder_5_to_3v3.kicad_sch, harp_core_rp2040_w_isolated_usb.kicad_sch, harp_treadmill.kicad_pcb, harp_treadmill.kicad_sch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]
2023-11-14 draft v0.1 pcb
    [harp_core_rp2040_w_isolated_usb.kicad_sch, harp_treadmill.kicad_pcb, harp_treadmill.kicad_sch, power_supplies.kicad_sch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]
2023-12-06 draft firmware
    [harp_core_rp2040_w_isolated_usb.kicad_sch]
2023-12-22 update board for v0.2.0
    [harp_treadmill.kicad_pcb, torque_load_driving.kicad_sch]
2024-01-10 update pcb to v0.2.0
    [harp_core_rp2040_w_isolated_usb.kicad_sch, harp_treadmill.kicad_pcb, torque_load_driving.kicad_sch, torque_load_sensing.kicad_sch]
2024-01-10 draft lid
    [1455L801_lids.SLDPRT]
2024-01-10 add lids
    [1455L801_lids.SLDPRT]
2024-01-10 update lids
    [1455L801_lids.SLDPRT]
2024-01-10 add lid dxfs
    [1455L801_lid_data_side.DXF, 1455L801_lid_io_side.DXF]
2024-03-08 add bulk sensor reading example
2024-03-08 add separate read-sensor example
2024-03-21 Standardize folder structure across allen devices
2024-06-14 add comment about race condition
    [harp_treadmill.kicad_pcb]
2024-07-25 add filter to torque limit sensing; bugfix reg_count
2024-08-21 Update device spec to latest firmware updates
2024-08-27 add trim to enclosure
    [1455L801_lid_data_side.STEP, 1455L801_lid_io_side.STEP, 1455L801_lids.SLDPRT, 1455L801_lids_and_trim.SLDPRT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]
2024-09-25 draft brake calibration scripts
2024-09-25 draft brake calibration code
2024-09-25 update silkscreen size; add mating connector note
    [encoder_5_to_3v3.kicad_sch, harp_core_rp2040_w_isolated_usb.kicad_sch, harp_treadmill.kicad_pcb, harp_treadmill.kicad_sch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]
2024-09-25 update brake calibration script
2024-09-25 draft working calibration script
2024-09-25 update calibration readme
2024-09-25 add calibration output-to-csv option
2024-09-25 update calibration script
2024-09-25 draft curve fit
    [test_rig_treadmill.csv]
2024-09-25 update pcb and schematic
    [harp_treadmill.kicad_pcb, torque_load_sensing.kicad_sch]
2024-10-11 add rrio note about ad8226
    [torque_load_sensing.kicad_sch]
2024-11-10 Favor harp-tech as source of device schema
